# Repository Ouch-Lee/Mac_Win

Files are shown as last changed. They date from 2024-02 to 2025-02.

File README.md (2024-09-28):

# Mac_Win
This repository is used to share files between my mac and win

actually it has been the primary repository for surgical robot project

## TODO

一个完整的手术机器人系统的设计主要包括如下内容：

* 机器人机构研究
* 机器人控制研究
* 图像引导和路径规划研究
* 人机交互研究。研究操作者、机器人、患者之间的人机交互操作机制，改善人机工效。

目前机械结构大致已经搭建完毕，后续主线任务不应该在机械设计上，而是搭建整个手术机器人系统

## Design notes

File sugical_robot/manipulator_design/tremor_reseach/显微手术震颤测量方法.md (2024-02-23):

# 显微手术震颤测量方法

[链接](https://onlinelibrary.wiley.com/doi/abs/10.1002/rcs.1717)

## abstract

* 震颤是执行精细运动任务（如显微外科手术）的主要障碍。传统测量不涉及代表显微外科手术的任务，都是静态测量
* 文章主要内容还是设计了量化手术测量的装置
* 8-12Hz，医生没有普通人明显
* 吹牛逼

## introduction

这个部分更为详细的介绍了手术中的震颤，文章强调什么呢，以前的人测量震颤都是关注静止的（**这里引用了很多论文要不粗略看一下？**），但是实际手术更多需要运动，如何在运动中分析抖动？（**那如果让我来写论文，我应该关注哪个呢？还是两个都关注？**）

## method

这个部分和上一篇论文基本一样

重点是如何去分析获得的信号

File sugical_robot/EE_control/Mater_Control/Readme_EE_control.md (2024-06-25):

# Readme_EE_control

这部分代码用于主端下位机STM32的控制；代码主要的目标是读取电机状态，控制电机运动，使用DMA读取多个传感器的信息

控制逻辑如下：

预动作：先关闭后开启（**搞定**）

上电后电机回零到初始位置[a1, 0, 0, 0] （需要写位置控制代码）**已经实现了**

是否需要检查一下电机是否正常工作？

用手捏pincher两次，作为开始控制的信号；当检测到gripper端编码器两次大幅度运动时（写检测和判断代码）

先实现DMA，然后写一下这个判断逻辑

* 成功实现DMA功能，现在将其移至到整体代码中-成功整合，遇到报错link 找不到函数的问题，因为没有添加对应=》成功整合代码；
* 

开始工作，进入while循环 ；首先使用50Hz的频率采样读取电机角度，编码器角度

* 电机角度读取的原理是CAN的中断，向电机发送命令帧后会自动返回回复帧，并通过中断获取；所以重点是处理函数：在处理函数里面根据第一帧的数据进入不同函数处理：
  * 多圈角度：0x92
  * 单圈角度：0x94
  * 编码器一堆字节：0x90
  * 电机状态：0x9C
* 将读取的12个角度编码，通过CAN发送到从端单片机（这里写好了，但是需要整理）
  * 将8+4存在同一个数组中，并使用CAN_send_函数发送（已经写好了，测一下延迟）

## 电机控制

需要借助电机实现的功能如下：

```C
float theta_0[2] = {0.0, 0.0}; // 假设两个编码器的初始角度都为 0 度
float theta_1[2] = {45.0, 55.0}; // 假设两个编码器的目标角度分别为 45 度和 55 度

// 编码器状态枚举
typedef enum {
    AT_THETA_0,
    MOVING_TO_THETA_1,
    AT_THETA_1,
    RETURNING_TO_THETA_0
} EncoderState;

// 用于记录每个编码器达到theta_1的次数
int theta_1_reached_count[2] = {0, 0};

// 检测编码器是否到达目标角度，考虑误差范围
bool is_at_theta(float current, float target, float error_range) {
    return fabs(current - target) < error_range;
}

int main() {
    printf("Starting encoder movement detection.\n");

    // 初始化编码器状态
    EncoderState state[2] = {AT_THETA_0, AT_THETA_0};

    // 无限循环，直到两个编码器都达到theta_1两次
    while (true) {
        for (int encoder_id = 0; encoder_id < 2; encoder_id++) {
            float current_angle = read_encoder_angle(encoder_id);

            switch (state[encoder_id]) {
                case AT_THETA_0:
                    if (current_angle > theta_0[encoder_id] + (theta_1[encoder_id] - theta_0[encoder_id]) / 2) {
                        state[encoder_id] = MOVING_TO_THETA_1;
                    }
                    break;
                case MOVING_TO_THETA_1:
                    if (is_at_theta(current_angle, theta_1[encoder_id], 0.1)) { // 假设误差范围为0.1度
                        state[encoder_id] = AT_THETA_1;
                        theta_1_reached_count[encoder_id]++;
                    }
                    break;
                case AT_THETA_1:
                    if (current_angle < theta_1[encoder_id] - (theta_1[encoder_id] - theta_0[encoder_id]) / 2) {
                        state[encoder_id] = RETURNING_TO_THETA_0;
                    }
                    break;
                case RETURNING_TO_THETA_0:
                    if (is_at_theta(current_angle, theta_0[encoder_id], 0.1)) {
                        state[encoder_id] = AT_THETA_0;
                    }
                    break;
            }

            // 检查两个编码器是否都已达到theta_1两次
            if (theta_1_reached_count[0] >= 2 && theta_1_reached_count[1] >= 2) {
                printf("Both encoders reached theta_1 twice. Exiting loop.\n");
                return 0; // 正常退出程序
            }
        }
    }
}
```

```C
    // 电机数据解码
    if (rxbuf[0] == 0xA1) {
        int16_t tau = (int16_t)(rxbuf[2] | (rxbuf[3] << 8));
        int16_t speed = (int16_t)(rxbuf[4] | (rxbuf[5] << 8));
        uint16_t position = (uint16_t)(rxbuf[6] | (rxbuf[7] << 8));

        // 根据接收到的ID更新电机角度值
        if (id > DEVICE_STD_ID && id <= (DEVICE_STD_ID + 5)) {
            // 更新received_data数组中的角度值
						switch (id) {
								case 0x141: {
										received_data[id - DEVICE_STD_ID - 1] = (double)position / 65535.0 * 360.0 - 185;
										break;
								}
								case 0x142: {
										received_data[id - DEVICE_STD_ID - 1] = (double)position / 65535.0 * 360.0 - 322;
										break;
								}
								// 可以根据需要添加更多的case语句
								default:
										// 可以在这里处理未匹配到ID的情况
										break;
		}
            
        } else {
            printf("Received message with unexpected ID: 0x%03X\n", id);
        }
    } else {
        printf("Received message with wrong header byte: 0x%02X\n", rxbuf[0]);
    }
```

使用读取多圈角度的命令，出现bug：当角度为负数时不是负数而是

* 该问题已经得到解决，但是原理我并不懂（后面需要继续搞明白这一块

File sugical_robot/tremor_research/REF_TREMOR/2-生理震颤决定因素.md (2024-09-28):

# 生理震颤决定因素

## 摘要

目的:外围机械共振因素和中枢机制可能在生理性震颤(PT)的产生中发挥作用，这一点已经得到了很好的证实。此外，还假设受试者的年龄和性别等属性可能会影响PT。本研究旨在量化这些对PT的影响。**（主要是研究上述因素对生理震颤的影响）**

研究方法：对117名20至94岁的正常受试者进行生理手和手指震颤测量，使用加速度计和前臂弯曲肌和伸肌表面肌电图记录。在有体重和没有体重时测量手部震颤，在手臂伸出、前臂支撑和手支撑时记录手指震颤。测量每位受试者的手体积和握力。**（测量手部震颤的方法可以作为学习目标）**

结论：

增加惯性(平均5.2 Hz)可显著降低手部震颤频率(平均7.7 Hz)，且与手量呈负相关，而与握力无关。手指震颤显示，根据手臂的位置，最多3个和至少2个不同的频段(1±4,6±11和15±30 Hz)分别反映整个手臂，手和手指的共振频率。

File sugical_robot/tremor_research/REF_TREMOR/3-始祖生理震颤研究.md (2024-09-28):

# 始祖生理震颤研究

## 简介

简介主要引出论文话题——有人觉得生理震颤主要由脊髓决定，有人认为是大脑，但是频率确实是10Hz左右

研究方法：

* 使用加速度好于位置
* 介绍了很多当时技术局限性使用的方法，已经不具有实时性了

## 结论

正常成人生理性震颤的运动速率和记录部位与频率的关系

通过记录腕关节肌肉信号，得出振动频率的结论——7-12Hz

除了手部，身体其他位置也会存在振动

肢体放在偏下时的振动振幅大于被抬起来

手腕/肩膀添加负重时，抖动会发生改变

小孩也有抖动，这些抖动发生在腕部、肩膀、脚踝，膝盖（以前没人做过）

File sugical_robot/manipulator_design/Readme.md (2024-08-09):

## 论文说明

2-Technical review of the da Vinci surgical telemanipulator：达芬奇手术机器人专利

3-A novel pich grip design：设计了一种权衡手指捏握和手柄的grip

4-DaVinCi_patent：达芬奇手术机器人专利

5-hand_fitague_research：很早的一篇文章（1979），研究了手部在几种状态下肌肉震颤情况，量化的方式是通过记录什么肌电图

6- 一篇解剖学相关的文章，论述了手部的两种姿态

7- 一篇关于pincher grip的专利

8-一篇介绍仅紧凑master manipulator设计的论文

9-[哈工大一遍优化主端手术机器人的文章](https://ieeexplore.ieee.org/abstract/document/8848374)

10-[稍后再看](https://link.springer.com/article/10.1186/s12938-018-0601-6?fromPaywallRec=false)

11-[一篇把gripper讲明白了的IROS](https://ieeexplore.ieee.org/document/8202159)

12-[还有专门研究gripper的？](https://www.researchgate.net/publication/271547893_Effect_of_load_force_feedback_on_grip_force_control_during_teleoperation_A_preliminary_study)

13-[很捞但至少它是真的做gripper的](https://ieeexplore.ieee.org/abstract/document/7177760)

14-[一篇和我做的很像的all-joint-control的master device](https://link.springer.com/article/10.1007/s11548-016-1352-0)

15-[一种圆柱体gripper？](https://ieeexplore.ieee.org/abstract/document/7759149)

16-[4DOF抓手力反馈研究](https://ieeexplore.ieee.org/abstract/document/4145189)

17-[MIS抓手力反馈实现](https://ieeexplore.ieee.org/document/10058553)

18-[自己做一台达芬奇](https://ieeexplore.ieee.org/abstract/document/6907809)

19- [master_console_review.pdf](master_console_review.pdf) 

### combined-grip-handle grips design

这篇文章讨论了目前主流的两种grips——pinch类型（以达芬奇手术机器人为代表）和power类型（以sigma7）为代表分别存在优缺点，前者精度更高，但是使用时更加费力；后者则刚好相反，因此作者通过一些设计权衡两者之间的优缺点

首先提出了将pinch安装在handle上的概念，通过一个转动副和一个移动副连接（被动的没，相当于一个调节的作用），通过设计对照试验，验证了有这个自由度好一点

整篇论文大部分时间都在介绍实验以及实验结果，通过多组对照组，得出时间相关的结论

### Prehensile Movement of HUman hand

该文研究了人类手部的可动性能力，包括不同类型的握持方式和手腕的运动。该文的主要结论是，手部的握持方式和手腕的运动是根据任务目标来选择的，任务的要求可以分为力量和精度两个方面，而手部的可动性能力可以满足这些任务的要求。此外，该文还指出，人类手部的简单和通用性质是其进化的结果，而过度专门化会限制手部的其他可能用途。

## Hamlyn CRM: a compact master manipulator for surgical robot remote control

introduce：该部分先介绍了主流手术机器人主要由三部分组成：a master control console with interactive manipulators, a slave surgical robot with articulated instruments and a feedback system with vision and other sensing modalities.；之后介绍了主从结构的特点，但是不够紧凑，所以这篇文章用了传感器融合技术；同时重点介绍了他们手术机器人模型的映射策略

* 机械结构

  通过matlab的运动简图可以看出大致原理，三个正交轴实现手朝向的变化，一个线性轴+万向节实现空间位置改变

* 运动学

  运动学较为简单

* 传感器融合

  * 两个imu+两个霍尔传感器
  * 如何进行处理传感器数据

* 末端添加光标，结合NDI光学跟踪系统验证末端精度

* 主从映射策略

  * 主从系统那个图做的很好，很具有借鉴价值
  * 所有传感器信息使用到了ROS发布
  * 介绍了 主-视觉坐标系-从坐标系之间的变化（由于还没有研究视觉坐标系，这里先跳过）
  * 映射模式：位置模式采用P模式，姿态采用绝对（直觉映射）和增量控制两种模式，两者各有优势
  * 

## 11-Master manipulator designed for highly articulated robotic instruments in single access surgery

**introduce**：因为主从机器人的性能很大程度取决于master device 的性能，这个设计是为了解决工作空间不匹配，以及缺乏重要关节被限制的信息（可能他就是想说明同构关节的好处，能够让操纵者知道哪个关节受到了限制）；关节处设计一个力传感器主意挺不错，可以通过力的方向判断运动方向，结合电机辅助操纵者运动

introduce: 先介绍了手术机器人主从系统的被广泛应用的原因；后面介绍为什么要注重主端的设计：

An advanced slave system composed of highly dexterous instruments will ultimately not perform to its full potential if paired with an inadequate master system.

然后提出目前主流的手术机器人都是基于task space去设计，这样的缺点是 mismatch ，以及一些缺点

所以,the use of a dvice-specific master manipulator commanding the slave robot is **joint space** can be an attactive alternative。

后面介绍了几种joint-control的主端设备，但是缺点竟然是关节都是被动的？

**manipulator design:**

具体介绍了机械结构

**Workspace Analysis：**

绘制了主从工作空间的灵活程度（我是不是应该也分析一下？

Control system：

* 为了提示操纵者每个关节快到边界了，添加一些阻力
* 自身重力补偿
* 摩擦力补偿，这个等到自己要做的时候再仔细的看

## 12-研究gripper握力的文章

这篇会议论文刚好就是我现在在做的东西，可以带着critical thinking的眼观来审视这篇论文

文章主要想解决的问题是目前手术机器人的抓取严重依赖视觉反馈，力太大夹伤了，力太小又容易脱落。所以这篇文章就是研究如何控制握力

之前的工作是证明人手在抓取时手指的窝里和手上的载荷相关；视觉仅能进行预估，不如触觉准确；还有一些别人做的实验，说明平移的反馈了不如抓取的反馈力，这不是废话吗

## 16

1. **研究目的**：文章旨在确定在执行远程操作任务时，握力反馈与笛卡尔（平移）力反馈对操作者的影响。
2. **系统开发**：研究者开发了一个系统，为3自由度（DOF）的Phantom触觉设备主机增加了额外的握力反馈DOF，并且在Phantom触觉设备从机的每个“手指”上增加了6-DOF力/扭矩传感。
3. **实验设计**：用户在执行一个软性插孔任务时，会接触到不同的力反馈条件：(1) 全力反馈，(2) 仅平移力反馈，(3) 仅握力反馈，以及 (4) 无力反馈。实验结果显示，在增加握力反馈的3-DOF远程操作器中，平移和握力的施加水平是解耦的，这可能是由于内部和外部手部力的动力学是解耦的。
4. **远程操作器的挑战**：当前的远程操作器，包括手术远程操作器，并不向用户提供完整的力反馈。力传感器的尺寸、消毒和生物相容性限制了在手术环境中使用从机器上完整的力感应的可行性。
5. **实验方法**：五名右手受试者使用4-DOF远程操作器执行简单的操作任务，即抓取一个矩形泡沫“插孔”并将其插入泡沫块中的矩形孔中。实验中提供了四种不同的力反馈条件，每种条件都由受试者随机顺序重复五次。
6. **实验结果**：方差分析（ANOVA）表明，力反馈显著影响平均施加的平移力和平均施加的握力（p < 0.0001），但对完成任务的时间没有显著影响（p = 0.144）。实验不支持假设1和假设2，即平移力反馈不会显著影响施加的握力，反之亦然。
7. **结论**：文章提出了一个使用两个Phantom触觉设备的4-DOF远程操作器，该设备具有可附加的夹持机构，能够提供4个DOF的力反馈。研究表明，在没有提供力反馈的DOFs中，平移力反馈和握力反馈在调节力的能力上是解耦的。在需要最小化Cartesian力反馈和握力反馈的情况下，显然需要全反馈。
8. **未来工作**：未来的研究将包括对能量观测器和环境建模的研究，以减少部分力反馈对用户的负面影响，并确保具有传感器/执行器不对称性的远程操作器的稳定性。

文章的研究对于理解和改进远程操作器，特别是在手术远程操作领域的力反馈设计具有重要意义。

### 商用手术机器人

根据搜索结果，以下是一些国外与达芬奇手术机器人类似的腹腔镜手术机器人：

1. **图迈®腔镜手术机器人系统**：由上海微创医疗机器人（集团）股份有限公司研发，已获得欧盟CE认证，可用于泌尿外科、普通外科、胸外科、妇科内窥镜手术。该机器人具备力觉感知呈现组件、多层安全防护架构和先进的成像系统，提供10倍光学放大的高清视野，实现裸眼3D成像 1。
2. **MIRA 微型手术机器人**：由Virtual Incision Corporation推出，是首个用于腹腔镜手术的微型机器人，重量仅有900克，通过肚脐内的单个切口完成手术。MIRA平台专注于微创结直肠和下消化道手术，具有一次性末端执行器仪器、双极抓手和单极剪刀，以及柔性尖端机器人相机 2。
3. **美敦力的Hugo**：美敦力公司推出的Hugo手术机器人，获得CE批准上市，专为泌尿科和妇科手术设计。Hugo是一个模块化的多象限手术平台，结合了腕式器械、3D可视化和Touch Surgery Enterprise，旨在降低成本和使用障碍，提高外科手术机器人的普及率 9。
4. **Medrobotics公司的Flex Robotic System**：该系统可以导航接近180度的路径到达具有挑战性的手术目标，外科医生可以从稳定的手术平台部署3毫米铰接器械，扩大执行手术范围。该系统已于2014年获得欧洲CE标识，2015年获得FDA批准 2。
5. **TransEnterix公司的Senhance数字腹腔镜手术系统**：具有压力感知和触觉反馈系统，通过压力警报增强医生的感知。该系统在欧洲和日本获批上市，并已提交FDA审查 2。

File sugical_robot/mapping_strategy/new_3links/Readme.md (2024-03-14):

# Readme

* get_continuum_T: 求单个连续体末端相对于base的其次变换矩阵
* extended_two_links: 用于求解添加extended坐标系后二连杆的T（好像）
* check_two_orien: 看起来像在验证没有添加delta_x 前的映射
* check_paper_DH: 似乎添加delta_x后的映射，运行前需要先运行extended_two_links
* my_DH_matrix ： 用于求解主端运动学的其次变换矩阵

最终结果在 "Show rotation.m" 文件中展示

在运行该文件前，需要先运行“extended_two_links”+“check_paper_DH”

### STM32串口数据处理

* 传输的数据太多了，所以先进行了简单的采样处理 sampling_array 函数
* get_end_position 传入采样后的数据
  * 需要处理一下角度
  * get_one_P中计算全是整数的问题，将sym计算得到的数换到另外一个T_matix里面就行
  *

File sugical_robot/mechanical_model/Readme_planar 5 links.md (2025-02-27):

# Readme_planar 5 links 

提出第二代base结构，使用平面五连杆机构

## 平面五连杆结构的优势

## 运动学模型

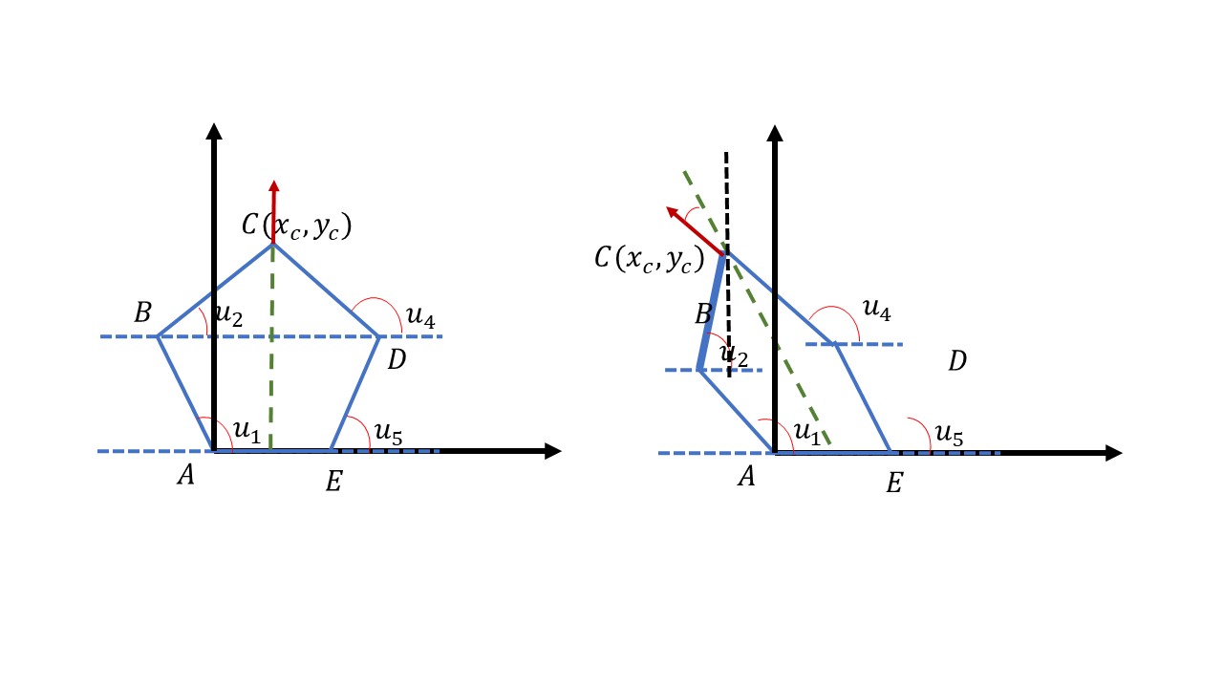
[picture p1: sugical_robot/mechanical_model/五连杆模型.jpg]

$$
x_b = l_1 * cos(\lambda_1),
    y_b = l_1 * sin(\lambda_1); \\
    x_d = l_5 + l4 * cos(\lambda_4),
    y_d = l_4 * sin(\lambda_4); \\
    BD = \sqrt((xd - xb)^2 + (yd - yb)^2) \\
$$

$$
\phi_1 = cos^{-1}(\frac{l_2^2 + BD^2 - l_3^2}{2*l_2*BD}); \\
\phi_2 =  tan^{-1}(\frac{yd - yb}{xd - xb});  \\
\alpha_2 = \phi_1 + \phi_2
$$

具体的实现可以参照[代码](E:\GitHub\Mac_win\Mac_Win\sugical_robot\mechanical_model\plannar_5_links\planar_5_bar_foward_my.m)

为了满足规范的角度规定（如下图），得到新的公式结果：
$$
\alpha_2 =( \phi_1 + \phi_2 ) - \alpha_1  \\
\alpha_3 = \pi - ( \phi_3 - \phi_2) - \alpha_4
$$



根据论文里面的公式，可以求解末端端点，但是

https://journals.sagepub.com/doi/full/10.5772/45683

[目前发现最早动力学推导论文](https://www.sciencedirect.com/science/article/pii/S0957415804000625)：现在没心情看

[用在打印机上的平面五连杆](https://www.sciencedirect.com/science/article/pii/S0736584512001214)：机械结构设计可以参考

## matlab实践

https://ww2.mathworks.cn/help/sm/ug/five-bar-robot.html

https://blog.csdn.net/qq_36014310/article/details/76924980

## 工作空间分析

得到五连杆的正向运动学模型后，通过循环的方法似乎可以得到原始的工作空间

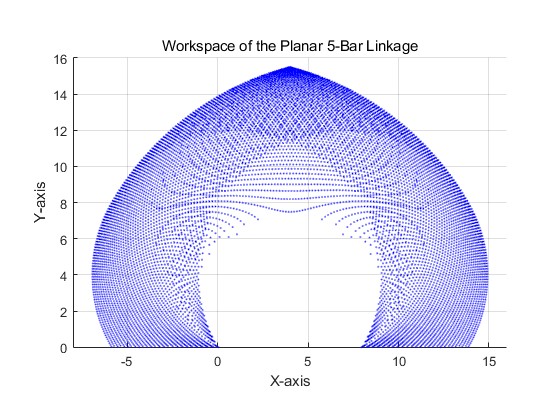
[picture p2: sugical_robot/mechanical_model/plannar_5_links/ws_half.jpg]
ws_half


上面是不考虑对称位型的工作空间，下面红色是添加对称位型后的工作空间；其实也就多了中间一小部分，因此为了简化问题，这一部分确实可以舍弃，因此【需要考虑一些机械限位】

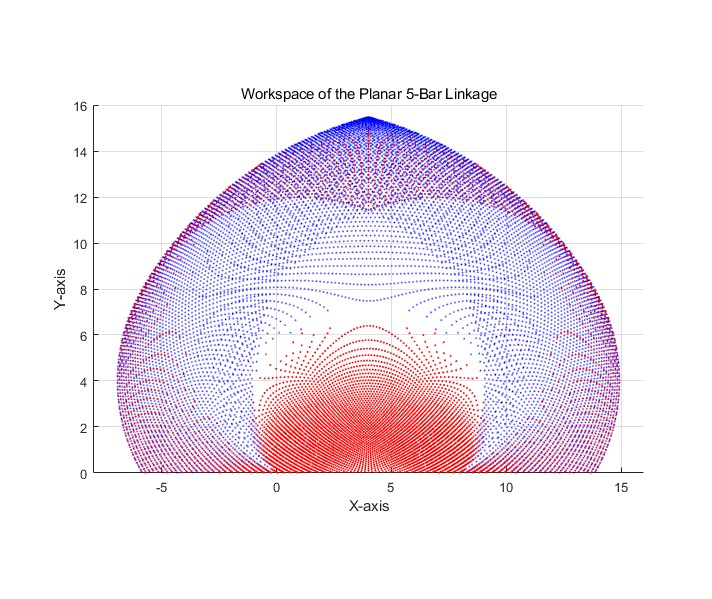
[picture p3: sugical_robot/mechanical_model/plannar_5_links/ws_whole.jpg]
ws_whole


相比之下，通过缩短两个关节之间的距离，可以明显增大工作空间

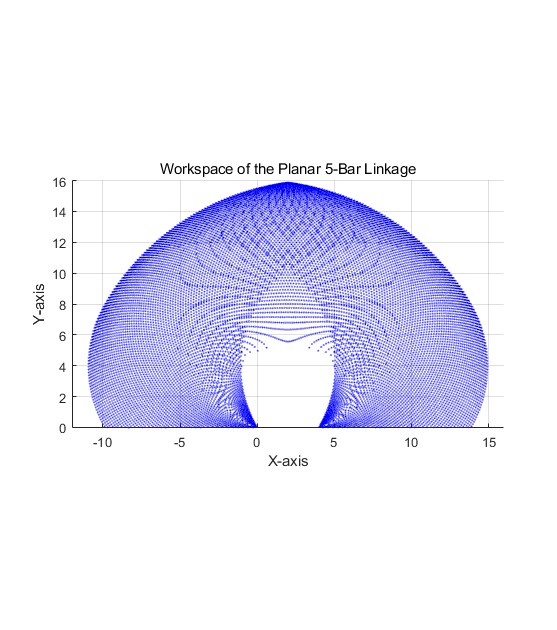
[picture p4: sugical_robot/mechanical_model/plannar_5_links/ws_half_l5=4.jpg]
ws_half_l5=4


## 结构设计

[日本轴承](https://detail.tmall.com/item.htm?spm=a21n57.1.item.2.5ae5523ccEkvGh&priceTId=215041aa17187626641891929e1a65&utparam=%7B%22aplus_abtest%22:%22dd09899006de88438ba666a726a98146%22%7D&id=668412789062&ns=1&abbucket=8&skuId=4809943724973)

[便宜一点的](https://detail.tmall.com/item.htm?spm=a21n57.1.item.48.5ae5523ccEkvGh&priceTId=2147bf3617187636843351715e1a6c&utparam=%7B%22aplus_abtest%22:%22d2c9aabf4e6b96251b2b7bc117ae65de%22%7D&id=611796709407&ns=1&abbucket=8&skuId=4777422306655)

目前计划选择  I5o14h5的 => 改为 I5O16H5，根部使用标准轴承 7000AC: 10 26 8

深沟轴承换为角接触轴承 需要 10 -15 个

轴承：

* [x] 推力轴承i6o19 x 6
* [ ] 

需要的螺栓：

* [x] M6 x 18 / 20 + 30
* [x] M4 x 26 + 20
* [x] m3 x 5
* [x] m2.5 x 10 \12
* [x] m2 x 20 + 8
* [x] m2 沉头 x 5
* [x] M6螺母
* [x] M4 螺母
* [x] phi6塞打螺栓x20
* [x] phi6塞打螺栓x25
* [x] phi6塞打螺栓x40
* [ ]

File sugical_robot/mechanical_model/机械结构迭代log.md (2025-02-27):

# 机械结构迭代log

5-26号装完第一版以后存在如下问题

* 配重不准（）

* [x] 替代电机的部分连接不稳：没有2.5螺母，轴承过盈效果不佳，最重要pitch连杆固定不住

  添加了2.5螺母，pitch连杆添加螺母固定，增强轴承过盈效果

* [x] 编码器孔是4

* 电机安装座通通错位了

* [x] 横向电机螺栓未考虑 用16的

* [x] 纵向齿条加固件干涉

* [x] 横向电机没有螺母

* 切割板没有电机安装孔，导轨安装孔为M3

* [x] 手柄main部分和齿轮干涉

修改

* 首要需要解决的是main部分需要：

  * [x] 编码器固定孔
  * [x] 上下螺母槽
  * [x] 齿轮卡住的问题
* 2.5螺母
  * [x] 购买
* 齿条

## 8-11完成初步结构后完善

### 悬臂梁配重

经过大致计算，关于转轴的力矩为 8360 g*cm，整体重量为750g，等效质心距离为11.15cm， 平均到两个杆

经过力学分析：
$$
F_N - F_p = F\\
F_N * l_2 + F_p * l_1 = F*L \\
F_N * (l_1 + l_2) = F*(L + l_1) \\
F_p * (l_1 + l_2) = F*(L-l_2) 
$$

通过有限元分析，使用铝合金 7075 足以满足要求，不会产生明显偏转

除此之外，添加一定重量的配重，目前的想法是每边添加一个500g的配重

之前只考虑倾覆力矩其实还有很明显的压力，所以需要添加一个推力轴承，这样也不会出现明显下倾的趋势了

* 电机与转轴适配性的问题：

目前的电机不一定能满足控制要求，但是理论上只要控的好，可以收敛不抖动；为了考虑性能，还是需要做到转轴适配不同电机？

感觉成本也不是很高，一体化可以避免配合间隙，尽量一体化

* 左右需要错开
* 旋转不能碰到base，但是杆长又不能延长了，所以得有一个偏置

## 整体机加工

之前三连杆部分采用的树脂3D打印，时间长了褪色，而且存在虚位较大的问题；

因此在重新设计了符合机加工的零件后，绘制了对应的[加工图纸](E:\master_console_ver3\图纸\2025-1加工)

第二批机加工需要准备零件：

| 零件          | 数目          |      |
| ------------- | ------------- | ---- |
| 杯头M3 x 10   | （12+8+8）x 2 |      |
| M3x6x0.8 垫片 |               |      |
| 平头M2.5 x 8  | 5x4 x 2       |      |
| M3手拧螺丝    | 4             |      |
| 平头M3 x 6    | 8 x 2         |      |
| 平M2X6        | 8x3           |      |
|               |               |      |

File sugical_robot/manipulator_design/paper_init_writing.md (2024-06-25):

# 论文撰写—一种应用于NOTES手术机器人的外骨骼式主操作台设计

## 摘要

这篇文章主要介绍一种应用于自然孔腔手术(NOTES)手术机器人的外骨骼式操纵台的设计。手术机器人系统整体采用主从式驱动映射策略，设计该结构的目的，力求保证手术医生手臂舒适、不影响手术医生手部自由运动的情况下，将手术医生手臂与手动作以直觉的方式映射到从端手术机器人。文章主要介绍该装置在结构上的创新性，舒适性，及其可行性。并从软件和硬件两个方面介绍了该装置在消除手术过程中手部颤抖的贡献；根据预期的直觉映射策略，推导主端驱动空间到从端构型空间的映射关系，并在仿真中验证了映射的可行性。

**3-8：结建立的动力学模型 of master console，我们使用我们的设备对手部生理震颤提出了评估，and address the hand tremor from both software and hardware perspectives** 

通过分析主从端的运动学模型，我们建立了合适的mapping strategy, which showcases the system's intuitive operation.

## Introduce

_____

		自然孔腔内窥镜手术是一种借由内窥镜通过人体的自然孔腔到达病灶位置的外科手术，自1957年第一台光纤内窥镜成功完成诊断手术以来[1]，内窥镜技术得到广泛关注和发展，19世纪70年代人们开始设想借助内窥镜完成一些简易手术，1980年  Michael W.L. 首次对12名儿童和19名成人描述了“无需剖腹手术的胃造口术”(**这里改成英文**)[2]，验证了内窥镜手术的可行性，由此学者开始尝试使用内窥镜完成更复杂的手术，并于2005年被正式提出NOTES的概念[3]。相较于开放的剖腹手术，NOTES存在诸多优点，可以避免开放手术带来的伤口感染和切口疝的问题[4]，因此可以实现更快的术后恢复，减轻患者术后疼痛等问题。

		早期的NOTES通过内窥镜及其配备的简易活检设备实现，只能进行简单活检和组织切除手术，为了完成更为复杂的手术，学者们设计了多种用于NOTES的手术机器人，它们通常具有相同的配置，集成摄像头的内窥镜主轴和从远端分支的两个手术臂 ，如  EndoSAMURAI[5]，Cobra[6], K-flex[7]。操作三角测量在柔性内窥镜手术中的灵巧检查和操作中起着至关重要的作用，该角度可以定义为两个仪器之间的远端姿势向量[8]，受限于结构，上述手术臂为单段连续体通常不具有良好的三角测量性，ANUBIScope[9], A flexible endoscopic surgical system[10] 将出口展开提供被动的三角测量性。

		尽管NOTES手术机器人已经成了医疗设备领域的热门研究对象，但现有关于其操纵台介绍的文章较少。目前商业主流的操纵台，如达芬奇手术机器人[11]和Hugo[12]，其操作台均为6自由度，而大多NOTES手术机器人有4自由度，两者存在不兼容的情况。为了避免自由度冗余，早期类似于EndoSAMURAI和Cobra的手术机器人采用纯机械式的摇杆（[下图](https://link.springer.com/article/10.1007/s00464-012-2173-z/figures/1)），在实际手术中需要多个人配合操纵，过于简单的操纵台使得医生使用体验不佳，这样导致手术效率低，安全得不到保障。设计不良的界面会降低外科医生的人体工程学效果，并会阻碍机器人的接受度[13]，这一点在微创手术机器人设计中已经验证。   [KFLEX](https://onlinelibrary.wiley.com/doi/abs/10.1002/rcs.2078) 设计了一种简易的三联杆结构用于柔性臂的控制，可以实现更易让操纵者接收的“直觉控制”，但是结构设计过于简单，没有考虑人体工程学的问题，且没有考虑操作三角性的问题。

	受前人工作的启发，我们提出了一种可以控制三角测量性的内窥镜双通道手术机器人模型，它由远近两段连续体组成，近端的偏转提供主动的三角测量性，同时可以增加手术时的灵活性，近端和远端协作完成手术动作；并根据该模型自由度设计了一种外骨骼式的手术机器人操纵台，可以利用人体手臂的其中5个自由度一对一控制手术机器人的关节，实现高效的直觉控制。在进行第一版样机测试时发现操纵者手部存在明显的生理抖动，为了改善抖动引起的末端震颤，我们在硬件和软件层面提出了改善方法；通过建立主端两端运动学模型，我们推导了从操纵台的驱动空间到末端执行器构型空间之间的映射关系，并在matlab中验证了映射关系的正确性。

	本文的结构如下：在第二节阐述了主从两端自由度分布，以及对操作台的机械结构设计进行介绍；第三节主要关注在NOTES手术机器人在主端震颤过滤的东线；第四节推导了操纵台到柔性手术臂之间的运动学映射；第五节对全文进行了总结。

Flexible instruments with steerable heads and multi-instrument flexible devices are difficult to control manually using a single operator.[13](https://ieeexplore.ieee.org/abstract/document/9779312)

##  MECHANICAL DESIGN

### 主从端自由度配置

设想的从端手术机器人配置如下（Fig2(a)）：柔性机械臂搭载在双通道的内窥镜上，其近端连续体由同向的单元连接而成，在一对cable的驱动下可以朝两侧弯曲，以增大远端连续体之间的间距，提供较好的三角测量性；远端连续体相邻的单元正交排布，由两对cable驱动，具有两个方向偏转自由度，末端器械通过微型轴承连接在远端连续体上，具有绕轴旋转和开合的自由度。

主端操纵台的功能是精准捕捉并映射操纵者控制指令，力求满足人体工程学设计，避免影响手术医生上肢自由运动。合理的自由度布局能避免复杂的映射策略，使得外科医生直观的进行操作，以减少学习曲线并提高手术的安全可靠性[]，因此master console，末端执行器与人体手臂三者之间自由度分布与极为类似, 如fig2所示。这种布局使得surgeon和master console之间有较好的适配性的同时，又让surgeon能舒适的控制surgical arm。

三者之间自由度的联系如下：操纵者将手肘“固定”在“搭载台”上以后，利用肩关节和手肘关节配合实现前后和内外翻转运动，并驱动操纵台“搭载台”下的两个正交的平动关节，对应手术机器人末端的前后伸缩，以及负责调控三角测量性近端连续体的偏转；手指握在pincher formation处，配合手腕的关节实现yaw,pitch, rolling 三个方向的运动，驱动操纵台前端三轴交于一点的“三连杆”对应的旋转关节，实现执行端前端连续体的两个方向偏转及其末端手术器械的绕轴旋转。

备注：

2-26：自己修改了一遍，没有经过gpt润色

### 设备实现

___

操纵台两个正交方向的平动均由两根平行的**导轨滑块**（MGW9，中国江苏）实现，相对于K-FLEX中单个导轨的设计，间隔一定距离的平行导轨可以避免手臂搭载时压力产生的倾覆力矩，每对导轨上的板子多采用铝合金材料，通过验证可以满足强度校验；导轨带来顺滑移动的同时，也带来了系统不稳定的问题，轻微的扰动即可导致末端出现预期以外的运动，因此在上述结构基础上，每个方向的平动都使用连接了**无刷电机**（KMTECH，中国上海），并使用齿条齿轮机构作为传动机构。相对于编码器，在每个关节处配置无刷电机的好处是，关节抗外界干扰能力更强，同时电机能够实现更为复杂的控制，使得操纵台不仅是一个运动采集机构，同时也能实现一些交互控制，例如较为成熟的变阻抗控制，使得平动的关节的可以灵活的改变。

与hand交互的三连杆，在原理上它与K-FLEX一样，但在此基础上我们做出了许多修改：首先我们额外增加了两条镜像连杆以及一些**“配重砝码**”，这样使得外部更美观，更重要的是增加结构的平衡性和稳定性，除此之外，更好的力量传递和控制是双边结构相对于单边结构的一个重要优势，双边结构可以实现分布式力量传递，即将力量从两侧均匀传递到目标区域，是可以让操纵者的操纵更加顺滑。

前人设计的“finger gripper”结构通常是搭载在rolling连杆上的一个钳子形状的gripper，一般操纵者使用大拇指和食指握住以控制末端器械如镊子的开合，这使得其他手指则处于蜷缩的空闲状态没有被利用，我们提出了一种创新的【pincher formation】结构(Fig3(b))，给剩余三个手指提供抓握的同时，将它们利用起来完成其它的任务。这是一个类似于手枪把手的结构，操纵者可以使用中指扣住【扳机】，控制一些功能的开关，如手术时所必须的冲洗，吸收积液，充气等操作，为了灵活切换上述功能，在把手下端设置了一个【轮盘】来切换上述功能。上述零件受力较小，因此我们使用光造型树脂作为材料并以3D打印的方式制作，这种材料具有高精度、表面光滑、细节丰富、打印速度快以及可用于复杂结构的优点。

上述整个结构可以简化为串联的五连杆，Serial kinematic configurations的优点包括：机械结构更简单，有利于制造并减少潜在故障点，从而减少所需的维护量[ ]，同时运动学模型和动力学模型较为简单，为后续人机交互控制降低难度。

无刷电机的内部集成了驱动板，使得整体结构更为紧凑，且驱动板内部集成FOC算法，仅需向其发送指令即可实现多种模式的控制，包括增量位置控制，绝对位置控制，速度控制和力矩控制；同时电机还集成了精度为18bit的绝对值磁编码器；我们使用STM32嵌入式单片机作为控制板，通过CAN通信协议控制和读取电机的状态。

Here are the translations for the phrases you provided, suitable for use in a table and aiming for a natural and concise English expression:

yaw link rotation

- 肘部前后运动: Elbow Flexion/Extension
- 肘部左右摆动: Elbow Abduction/Adduction
- 手腕左右偏转: Wrist Ulnar/Radial Deviation
- 手腕上下偏转: Wrist Flexion/Extension
- 手腕绕轴转动: Wrist Pronation/Supination
- 底座前后平移: Base Anteroposterior Translation
- 底座左右平移: Base Lateral Translation
- 手术臂伸缩: Surgical Arm Extension/Retraction
- 近端展开: **Proximal Unfolding**  双臂展开怀抱和对应的反义词用英语怎么说
- 远端左右偏转: Distal Lateral Deviation
- 远端上下偏转: Distal Vertical Deviation
- 手术器械绕轴转动: Instrument Rotation
- 手术器械开合: Instrument Articulation/Open-Close

These terms are succinct and are commonly used in descriptions of mechanical movements, particularly in the context of robotics and biomechanics.

## 手部震颤抑制

震颤过滤是所有遥操纵的手术机器人需要共同面对的问题，在设备性能优良的情况下，操纵者手部的震颤成为了震颤的主要来源。这种震颤被称为生理性震颤（Physiologic Tremor），一种生理性现象，正常情况下每个人都会经历的微弱的震颤或颤动。这种震颤的频率在8-12Hz之间，通常肉眼通常无法感知，但在手术的条件下，生理性震颤是不可忽视的不利因素，The trend towards the use of ‘minimally invasive surgery’ also tends to amplify tremor effects, due to the longer lever-arm action of typical laparoscopic instruments[3-1].

Tremor mitigation is a critical challenge in teleoperated surgical robotics. When the equipment performance is excellent, the tremor of the operator's hand becomes the main source of tremor. This tremor, known as Physiologic Tremor, is a physiological phenomenon that everyone normally experiences as a weak tremor or flutter. The frequency of this tremor is between 8-12Hz and is usually invisible to the naked eye. However, under surgical conditions, physiological tremor is a disadvantage that cannot be ignored. The tremor effects are amplified, due to the longer lever-arm action of typical laparoscopic instruments.

为了对surgeon的手部Physiologic Tremor进行evaluation，首先需要记录震颤活动，通常 accelerometry, electromyography (EMG), and other signals (such as force or gyroscopic measurements) are acquired, digitized through an analog-to-digital board and analyzed. 这种方法的问题是设备测量精度不够高，不能直接反应手部震颤的效果。在这里我们让surgeon手握"finger gripper"，通过记录各个关节的位置信息，结合master console的正向运动学，计算末端在空间中位置的变化，从而记录手部的震颤。

【图片1：初步震颤】【图片2：悬空15min后震颤结果】

为了减弱指端生理震颤为手术带来的的影响，首先我们引入了卡尔曼滤波算法，在软件层面上削弱震颤信号的波形

### 自适应卡尔曼滤波

单个电机的角度信号可以看作一阶系统，建立其状态方程及其对应的参数如下：
$$
\begin{cases}
x_k = x_{k-1} \\
        y_k = x_k
\end{cases}
$$

$$
F_k = 1; \quad H_k = 1; \quad G_k = 0; \quad u_k = 0;
$$

$$
公式1；
$$
借助卡尔曼滤波算法进行迭代，可以较为明显的平滑由于生理震颤产生的抖动信号；
$$
公式2
$$
卡尔曼滤波作为最为人知的滤波算法具有适应性强、有效地处理噪声和不确定性、计算效率高的优点[ ]。但是该算法存在两个最缺点，首先它像PID控制一样，需要对公式2中的参数Q与R进行手动调试；其次该算法无法兼顾精度和滤波效果，Q与R的比值会影响滤波结果，比值越小表示预测值的权重越大，最终结果抗干扰越强，但是会丢失一定精度；反之，比值越大越靠近标准值，滤波的效果越不明显。对前一个问题，前人已经提出了许多改进的自适应卡尔曼滤波算法，对于后一个问题，我们在这里提供了一种简单的模型，通过记录前后两次采样角度差值的方法，简易的区分操纵波形和噪声，并根据差值实时修改Q与R：

**简化后：**

卡尔曼滤波可以有效的处理噪声，并具有计算高效的优点[ ]，但是该算法也存在两个问题，一方面公式2中的参数Q和R需要通过经验调试，另一方面滤波在平滑噪声的抖动时也会使得正常的操纵动作失真，（Fig_）；我们提出了一种自适应的改进KF算法模型，可以有效的避免上述情况；
$$
公式3
$$
其中avg为经验值，通过记录多次噪声取平均值而得，因此diff 与avg的比值表示信号振幅的大小，较大时表示操纵波形，较小时为噪声。图---对比了传统卡尔曼滤波与改良后自适应卡尔曼滤波的效果，图中可以明显看到改良后滤波算法即避免了传统滤波算法引起的失真，又达到了消除抖动信号目的：由于操纵指令和震颤的幅度相差很大，印使用$\alpha$ 记录前后两次位置的差值，差值小表示抖动，通过减小Q和增大R增强滤波效果，反之差值大时避免滤波影响输入指令，对应模型的结果展示在图_ 中。

图

The angular signal from an individual motor is modeled as a first-order system, with its state equation and related parameters detailed subsequently.

Employing the Kalman filter algorithm iteratively allows for the noticeable smoothing of jitter signals induced by physiological tremors. Renowned for its adaptability, effective handling of noise and uncertainties, and computational efficiency, the Kalman filter, however, faces two significant limitations. Firstly, akin to PID control, it necessitates manual adjustment of parameters Q and R, as delineated in equation 2. Secondly, achieving a balance between precision and filtering efficacy proves challenging. The filtering outcome is influenced by the Q-to-R ratio, where a lower ratio signifies a greater emphasis on the forecast value, enhancing interference resistance but sacrificing accuracy. In contrast, a higher ratio approximates the standard value more closely but diminishes the filter's effectiveness. While numerous adaptive Kalman filter enhancements have been proposed to overcome the first limitation, we address the second by introducing a straightforward model. This model easily differentiates between control waveforms and noise by recording the angular difference between two successive samples, thereby allowing for the real-time adjustment of Q and R based on this discrepancy.

### 搭载式

生理抖动产生的一个原因是手部悬空[ref]。通过观察可以发现，相较于手臂悬空状态，手臂被托举时操纵者手指末端的抖动幅度和频率更小，因此商业微创手术机器人的操纵台大多都设计了小臂托衬结构，该设计的另外一个优点是缓解手术时手臂维持长时间悬臂的疲劳。我们通过采集两种状态下电机的角度信息，计算出操纵台末端位置信息，并将其可视化在图中。

【这里需要实物，实验和分析】

手臂长时间滞空导致的肌肉疲劳会加剧生理抖动，这也是为什么大多商业的微创手术机器人的操纵台配备了小臂托衬结构，这里我们设计了一个肘部托举结构，其作用除了托举操纵者手部，同时也作为一个“操纵杆”用于控制操纵器在正交导轨上的位置。为了防止操纵者在移动手肘的过程中不产生相对滑动导致脱落，这里设计了一个“紧固”结构，其工作原理如下：在操纵者将手肘搭载在“carrying disc”上后，在重力的压迫下，“carrying disc”随直线轴承向下运动，该运动由连杆传递到sliders，并通过连杆使一端固定的“four link”产生变形，该变形的最终结果是“elbow protector”向内收缩，从而加紧操纵者的肘部，当操纵者想脱离该结构时，将肘部竖直向上抽离即可。这样就做到了肘部在“穿戴”与“抽离”之间的自由切换。

有一个致命的问题是，目前第二代的样机仍在搭建中，虽然能通过肉眼很直观的察觉到托举结构对手部震颤的改善，但缺少严谨的实验和实验结果来论证该结论，但这个空缺会在短期内完善。

Muscle fatigue caused by the arm being suspended in the air for a long time will aggravate physiological jitter. This is why most commercial minimally invasive surgical robot consoles are equipped with a forearm support structure. Here we have designed an elbow support structure, whose function is in addition to lifting. The operator's hand also serves as a "joystick" to control the position of the manipulator on the orthogonal guide rail. In order to prevent the operator from relative sliding and falling off when moving the elbow, a "fastening" structure is designed here. Its working principle is as follows: after the operator places the elbow on the "carrying disc",  under the pressure from the gravity of arm, the "carrying disc" moves downward with the linear bearing. This movement is transmitted to the sliders by the connecting rod, and deforms the "four link" fixed at one end through the connecting rod. The final result of this deformation is that the "elbow protector" moves toward Contraction inward to tighten the operator's elbow. When the operator wants to escape from the structure, he can pull the elbow straight up and away. In this way, the elbow can be freely switched between "wearing" and "taking off".

A fatal problem is that the second-generation prototype is still under construction. Although the improvement of hand tremor by the lifting structure can be intuitively detected with the naked eye, there is a lack of rigorous experiments and experimental results to prove this conclusion. This vacancy will be completed shortly.

## mapping strategy

这一部分主要介绍从主端操纵台的驱动空间[theta 1 ... theta 5] 到从端构型空间的映射策略，也即在检测到操纵者输入的控制指令后，从端柔性臂应该调整到什么位型。在手术机器人领域，目前主流的主从映射策略是保持主从两端姿态和位置相同：通过主端正运动学计算目标位姿，再使用从端逆运动学求解从端驱动空间。但是由于目前结构为5自由度，**为欠驱动状态（**Underactuated），因此主流方法不适用。我们采取的映射策略是保证主从两端的姿态保持一致同时伸缩按比例缩放，实现较好的“直觉操纵”。为了简化映射的复杂度，我们采用解耦的方法，将整体映射策略分远近两段的子映射，这个方法是可行的，在保证每个子映射策略符合“直觉操纵”的情况下，整体依然符合“直觉操纵”。

Fig.3 显示了主从系统的integrated kinematic drawing。对于主端刚性连杆结构，我们沿用DH标准为每个关节配置了坐标系，并构建了对应的DH table；

对于从端柔性连续体，使用常规的DH会带来巨大的计算复杂度，这里我们采用更适用于连续体建模的常曲率模型[ ]。在常曲率模型中，使用ks描述连续体偏离轴心的偏转角度，使用phi描述因为两个正交偏转叠加后产生的绕轴转动角度。对于如近端单自由度的连续体，phi可以是视作0不变。

前面两个自由度的运动较为简单，且两个映射完全解耦，因此分别进行简单的线性映射即可：

主端console纵向平动与从端柔性臂的“伸缩“，以及主端横向的平动与柔性臂”近端偏转“的映射可以完全解耦，分别进行简单的线性映射即可：
$$
公式
$$
其中theta_max为近端连续体偏转的量程，dmax为导轨移动量程；

为了保证主端R-P-Y“三连杆”与近端连续体姿态相同，一种方法是保证两者末端在其各自base坐标系旋下描述姿态的转矩阵R相同。 该问题通过代数直接求解的方法不仅计算量大，同时还会存在无解的情况，因此这里引入几何法对其进行求解。首先我们描述一组Fig(  )中的运动：初始坐标系O经过绕y_0旋转θ_3和绕x_1旋转θ_4后形成坐标系O_2；另一方面，初始坐标系经过绕z_0旋转ϕ后形成坐标系O_1^a，再经过绕y_1^a旋转ks后得到坐标系O_2^a，观察两次坐标变换所得坐标系的z轴重合。实际上前者就是描述的三连杆转动yaw和rolling方向上关节对应的坐标变化，而后者是连续体在绳子驱动下偏转后产生的坐标变化，z轴重合代表两者末端朝向一致，不过两个坐标系在x-y轴平面上存在一个偏置(Fig)；

同样的，我们将图(a)中)O2 和 Oa2提取出来，构建新的几何关系。只需要求解上述两个空间夹角，即可得到了映射函数，对于这两个问题均可使用【三余弦定理】，这是一种通过构建投影求解空间夹角的方法，具体的求解过程在附件A中给出。
$$
公式
$$
由此可得最终映射关系：
$$
公式
$$

根据公式(9)推导的函数，我们使用matlab在同一个坐标系下分别绘制主从两端的坐标系Fig6(c)，符合我们的预期，也即z轴重合，x-y平面存在偏执，再结合公式(10-13)求解的x，得到Fig6(d)的结果——两个坐标系完全重合，证明映射的合理性。

## 结论

在这篇文章中，我们提出了一种可以提供主动三角测量性的内窥镜的手术机械臂模型，并设计了一种适配于该类型手术机器人的穿戴式操纵台。在调试的过程中发现末端存在较为显著的震颤，并提出了两种方法改善生理抖动产生的震颤，为了之后主从遥操作做准备，推导了主从之间的映射函数。在后续的工作中会对样机的实体进行迭代，并完成空缺的实验，人机交互的控制策略正在研究中，致力于研发精准且舒适的主端操纵台。

## Reference

[1] Rosin, R. D. (Ed.). (1993). *Minimal access medicine and surgery: principles and techniques* (Vol. 1). Scovill-Paterson.

[2] Gauderer, M. W., Ponsky, J. L., & Izant Jr, R. J. (1980). Gastrostomy without laparotomy: a percutaneous endoscopic technique. *Journal of pediatric surgery*, *15*(6), 872-875.

[3] Rattner, D., & Kalloo, A. (2006). ASGE/SAGES Working Group on natural orifice translumenal endoscopic surgery: October 2005. *Surgical Endoscopy and Other Interventional Techniques*, *20*(2), 329-333.

[4] Giday SA, Kantsevoy SV, Kalloo AN. Principle and history of natural orifice translumenal endoscopic surgery (NOTES). *Minim Invasive Ther Allied Technol*. 2006;15:373–377.

[5] Fuchs, K. H., & Breithaupt, W. (2012). Transgastric small bowel resection with the new multitasking platform EndoSAMURAI™ for natural orifice transluminal endoscopic surgery. *Surgical endoscopy*, *26*, 2281-2287.

[9] Dallemagne, B., & Marescaux, J. (2010). The ANUBIS™ project. *Minimally Invasive Therapy & Allied Technologies*, *19*(5), 257-261.

[10] Kobayashi, T., Lemoine, S., Sugawara, A., Tsuchida, T., Gotoda, T., Oda, I., ... & Kakizoe, T. (2005). A flexible endoscopic surgical system: first report on a conceptual design of the system validated by experiments. *Japanese journal of clinical oncology*, *35*(11), 667-671.

[2-1] Kuniholm, J. F., Buckner, G. D., Nifong, W., & Orrico, M. (2005). Automated knot tying for fixation in minimally invasive, robot-assisted cardiac surgery.

## 一些细节+ 最终调整

* 到底叫console好还是manipulator好

* [ ] 修改tremor部分
  * [ ] 文字修改
  * [ ] 绘制FK模型，编写绘制末端位置的脚本，通过实验收集数据，得到xyz3维度图像
  * [ ] 添加KF后的结果的图像
  * [ ] 
* [x]

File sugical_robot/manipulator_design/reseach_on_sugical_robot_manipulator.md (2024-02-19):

# 手术机器人操作台控制器研究

key word: Surgeon Console Controls, manipulator, telemanipulator

感觉论文的核心还是应该围绕操纵端的设计，说来惭愧，连英文名都说不出来，现在知道了是manipulator（感谢gpt🙏）

### 精读达芬奇

```
Summary: The document is a technical review of the da Vinci surgical telemanipulator, a robotic system used in various surgical specialties. The review analyzes the strengths and weaknesses of the robot design based on published literature and patents. The main findings of the review are that while the da Vinci system facilitates complex surgical operations and has a low malfunction rate, it lacks haptic feedback and collisions between the robotic arms are a major limitation. Accurate positioning of access ports is also essential. The review concludes that knowledge of the technical aspects of the da Vinci robot is important for optimal use and highlights future trends in robot miniaturization and intelligent control design.

Main points:

- The da Vinci surgical telemanipulator is a robotic system used in various surgical specialties.
- The review analyzes the strengths and weaknesses of the robot design based on published literature and patents.
- The system facilitates complex surgical operations and has a low malfunction rate.
- The lack of haptic feedback and collisions between the robotic arms are major limitations.
- Accurate positioning of access ports is essential.
- Knowledge of the technical aspects of the da Vinci robot is important for optimal use.
- Future trends in surgical robotics include robot miniaturization and intelligent control design.
```

### 一篇外骨骼康复手腕万向节设计

锐评：这也能发，那我感觉我写好一点，比他还牛逼，不过可以认真读一下，学习一下它怎么展开写一篇会议论文

[原文](https://ieeexplore.ieee.org/document/6650459)

### 达芬奇三连杆结构

[专利出处](https://patents.google.com/patent/US6364888B1/en?oq=US6364888B1)

专利中把这个结构称为**[wrist gimbal]手腕万向节**；（为什么叫这个？）

专利写的很清楚，但是太啰嗦了，而我重点想研究手腕万向节

### 随口提一嘴：

[手持式同心管手术机器人](https://ieeexplore.ieee.org/abstract/document/9308920)：可以作为

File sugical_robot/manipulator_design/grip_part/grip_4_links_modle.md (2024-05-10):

# grip_4_links_modle

## 手柄四连杆部分力学模型推导

目标：测量操纵者手指提供的压力，并将测量的压力映射到末端手术器械的压力。常规力传感器无法适配这里尺寸较小的结构，尝试通过检测角度，以及力学模型测量指端作用力；

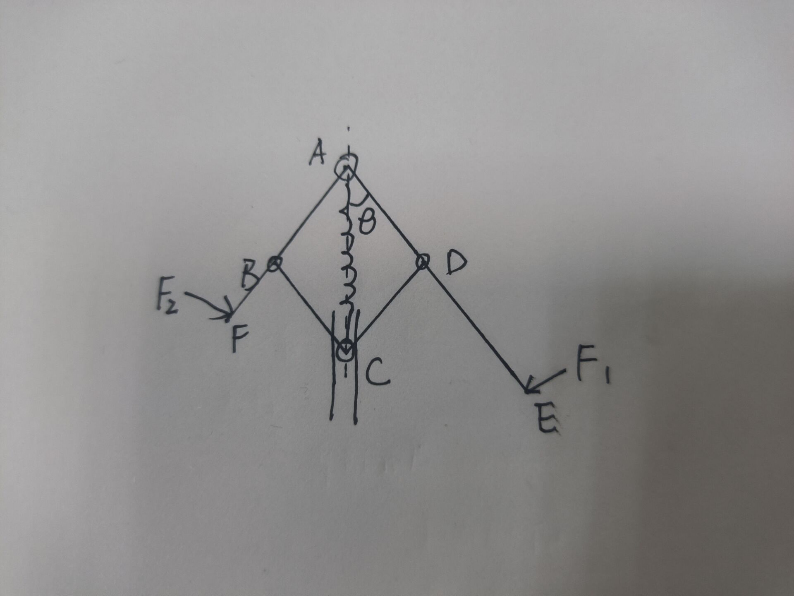
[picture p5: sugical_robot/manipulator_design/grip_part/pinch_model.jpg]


主要任务：推倒四连杆力学模型，找到$F_1, F_2$ 与 $\ang DAC (\theta)$ 之间的关系；

1. 对连杆AE受力分析，根据关于A点力矩平衡，可以得到$F_1$ 与 连杆CD对连杆AE的支持力$F_{N1}$ 之间的关系：
   $$
   F_1 L_1 = F_{N1} l_0 sin(2\theta) \tag{1}
   $$
   同理可得到$F_2$ 与 连杆CD对连杆AE的支持力$F_{N1}$ 之间的关系：
   $$
   F_2 L_2 = F_{N2} l_0 sin(2\theta) \tag{2}
   $$

2. 对连杆CD受力分析，将力分解到x，y两个方向可以得到等式
   $$
   (F_{N1} + F_{N2} ) cos(\theta) = F_{sping} + f \tag{3}\\
   $$

   $$
   (F_{N1} - F_{N2} ) sin(\theta) = F_y \tag{4}
   $$

其中，$F_1, F_2, F_{N1}, F_{N2}, F_y$为未知量，$F_{sping}$ 为拉簧弹力，和$\theta$ 相关，可以通过检测角度获得；4个方程，5个未知数，

.因此有无穷解；对于我们感兴趣的$F_1, F_2$ ，我们只能得到两者之间的关系：
$$
(F_1 L_1 + F_2 L_2 )= 2(F_{spring} + f) l_0 sin(\theta)
$$
这个公式对应的物理含义就是：维持每个位置所需要的力矩；

绘制出$(F_1 L_1 + F_2 L_2 )$ 关于 $\theta$ 的图像

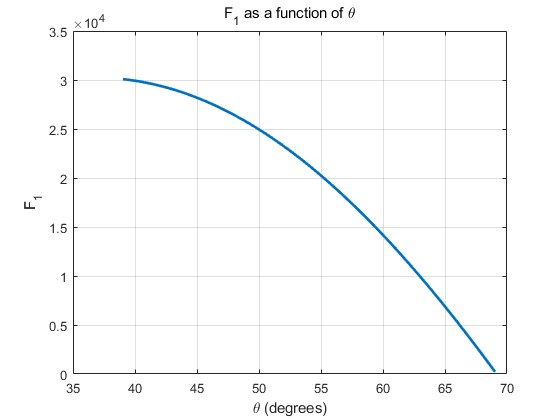
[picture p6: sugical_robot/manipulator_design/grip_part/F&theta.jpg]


## 拉簧选型

通过计算，可以确定弹性系数大致在65左右，且原长为20，半径为3，线粗0.5 => 72.34

注意，线径为0.4时，k = 23.7 (也可以买过来试一下)

有一个问题在于，这是比较理想的条件下，如果引入摩擦力呢对于4连杆部分，摩擦力的主要来源轴承关节、轮子上下表面摩擦，目前感觉不是很大，暂不考虑后面再改进吧；压簧的摩擦力主要来源于平移块与轴之间的摩擦力，

```matlab
% 这个脚本用于计算pinch部分拉簧的弹性系数等参数
L1 = 13.8; 
L2 = 18.5;
l0 = sqrt(L1^2 + L2^2); 

% 弹簧参数确定
l_spring_total = 20;
D_spring = 3;
l_spring = l_spring_total - D_spring; 

% 力矩长度
l1 = 58;
l2 = 33;

theta_i = 120 - rad2deg(atan2(L2,L1));
theta_f = theta_i - 30;
F_max = 250 * (l1 + l2); %tau: g*mm
F_spring_max = F_max / (2 * l0 * sind(theta_f));
delta_x = 2*l0*cosd(theta_f) - l_spring;
k = F_spring_max / delta_x;
disp('拉簧弹性系数：');
disp(k);
```

附加之前扳机设计时的选型：

**扳机拉簧选型：**

| 参数 | 长度(L) | D     | d       | k(g/mm)   |
| ---- | ------- | ----- | ------- | --------- |
|      |         |       |         |           |
|      | 15      | 5     | 0.3     | 4.02      |
|      | 15      | 5     | 0.4     | 19.18     |
|      | **15**  | **5** | **0.5** | **60.01** |
|      | 15      | 4     | 0.5     | 91.11     |
|      | 15      | 3     | 0.5     | 194.44    |
|      | 10      | 3     | 0.4     | 127.45    |
|      | 10      | 3     | 0.5     | 437.5     |

* 手指拉力测试

  轻轻的摁压力大概为300g；稍微用力500g

  300 —— 500 比较合适

以及摁压过程的行程 $x$ = 4;
$$
k = \frac{F}{\Delta x} = 186.864
$$

手指扣拉簧选型

* 经过拉力测试，作用到最远距离所需的压力 F1, F2 (暂定400)分别为，根据推导模型，可以确定在最大型变量时最大的拉力

#### 第二代迭代

之前计算的拉簧弹性系数明显过大实际购买的弹性系数，通过矫正，新的弹性系数确定在32左右

暂定 3 * 0.4 * 20 => k = 28 

### 夹紧机构压簧选型

设计夹紧结构的目的是让操纵者在感觉上能感受到一个明显的变化，知道确定目前是“力控模式”，同时稍微增大拉力程度可以防止施力过大；为了防止把对象捏爆，是不是要加一个**反馈？？？**

需要满足的条件：

* 完全压缩需要小于等于2.5，2.5太小，拓展了一下到5.5
* 夹紧（释放）状态长度为7.5；此时理想的压力为3~5牛

弹簧选型时主要需要确定长度l、直径D、线径d；弹性系数与三者之间的关系是——，反比，正比

通过确定了两组压簧，外径5，线径0.5，长度10/15；

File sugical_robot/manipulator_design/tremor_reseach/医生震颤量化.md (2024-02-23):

## 简介

这篇文章就是设计了一些实验来量化外科手术医生的tremor情况

结果：8-12 Hz范围内的大量振荡——因于生理震颤的增强。医生越做越强。

结论：除了量化了震颤；还建立了传递模型

```
所以这篇文章有看的必要吗；可以作为入门文章，研究一下临床医生震颤的情况；
一句话，我需要知道手术医生手抖到什么情况；如果有解决方案就更好了

```

## Introduction

虽然生理震颤很微弱，但是在不同情况下，或者不同姿势下；震颤的影响会不同的

手术就是一个特例，所以为什么临床手术医生要经过大量的练习做到手不抖，才能做手术（**这里要看更多论文论证**）

* 这篇[论文](https://sci-hub.se/10.1016/j.ncl.2009.04.003)简介又全面的总结了所有震颤，里面也强调了，影响医生的只有physiological tremor
* 

尽管如此，在微创外科手术时，经过[杠杆效应]，**末端的震颤会更加严重**（比如之前穿戴的手术设备，或者专用于微创的）

[提供材料](https://oup.silverchair-cdn.com/oup/backfile/Content_public/Journal/icvts/23/3/10.1093_icvts_ivw150/1/ivw150_Supplementary_Data.zip?Expires=1708564472&Signature=GCM00Gv7KwrgyrZTibInkPciJG6xMZSXOAGPSPsO4Pc1gYUEWIe3uKsTYYS6PdnoDhFFatcO5BW59RvPnff5HlTDEnykRK4SG7-sxaQY59gWd1~iDVoVLI-cC-3TUxkyLlbdEFTwo7w6Dee5k26sWekTZ-v~Sbsp1~zZ4CAYwDq4N1UkFAZ2sbPj3PRDZc6OwAHGW7TaeUiEXLP66asOeSEAZdzx1t1JDYgBG00C44BT3Kl71nMzJp7dSsnK6Rd-O7yCGgXDUCI77vdC1cbo2e6YG9OKsdkcK0AMJ~~cwh3EG5UaIv-2Mn~1VU50~agWKKjgR48DXKxDEgW6dfqI5g__&Key-Pair-Id=APKAIE5G5CRDK6RD3PGA)给了一些解决方法

作者说之前作者过于关注姿态追踪，而忽略了动态动作中的震颤

* application
  * 训练医生？你只是量化，有没有装置
  * 评估医生是否合格
  * 辅助年纪大可能

### Method

介绍了平台的设计，感觉很容易看懂，核心就是两个测量垂直方向力的传感器(为什么单方向的力传感器，可以测量出震动？？？)

### 信号处理

1. 分段
2. 带宽滤波
3. 计算bonferroni系数？
4. 计算关于手术和背景噪声的总结系数？（**没看懂**）
   1. 在8-12 Hz和14-18 Hz的频率范围内分别对频谱功率密度进行积分，分别表示与生理震颤和背景噪声相关的功率（我有点没看懂？）
   2. 与平台相互作用的所有时代贡献的总和。
   3. 总相互作用时间对总和贡献的归一化，并提取平方根
5. 

## 我的总结

读完这篇文章：

1. 他主要的内容是介绍怎么去设计一个实验评价和量化医生在手术时的震动；所以首先你要把他的方法总结出来，然后他做的肯定是很烂，需要改善的

   主要引用的这篇[文章](https://onlinelibrary.wiley.com/doi/abs/10.1002/rcs.1717)：

2. 简介部分提供了一些可以挖掘的信息

   * tremor里面之需要关注physiological tremor；其他医生不会太碰到；
   * 医生到底抖得有多厉害，好像说到现在也就是正常的8-12Hz
   * 文章只做到了竖直方向力的测量，并没有考虑其他方向，而是假设在所有方向振动幅度都一样
   *

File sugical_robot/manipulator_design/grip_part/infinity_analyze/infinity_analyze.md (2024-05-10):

# infinity_analyze

学习了在sw中使用有限元进行分析，首先对装配体整体进行了粗略的分析如下图：





由于装配体比较复杂，存在较大误差， 因此对形变较为明显的零件单独分析

| -           | 目前最大偏置 | 改良结构+尼龙 | 改良结构+金属 |
| ----------- | ------------ | ------------- | ------------- |
| pinch_right | 9            | 1.4 e-1       | 5.7 e-3       |
| pinch_left  | 4.7 e-1      | 2.57 e-2      | 1 e-3         |
|             |              |               |               |
|             |              |               |               |

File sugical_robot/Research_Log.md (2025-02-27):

# Research_Log

* 2025-2-17~2-24

  * 把新一版的结构搭建完（预计2.19~2.21）
  
    新加工的一批零件存在一些问题：
  
    1. 近端和远端均为右旋（大问题）
    2. 有一个远端连杆和左右连接件存在干涉，稍微打磨一下圆角就行了
    3. 远近连杆中间连接零件宽为11.78（小于所需的12.00），长为19.80小于所需的20.00，因此目前装不进去
  
  * 空余时间盯一下专利上传情况（新专利拖一拖）
  
  * 除颤的算法继续尝试
  
  *

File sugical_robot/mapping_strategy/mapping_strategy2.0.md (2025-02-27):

# mapping_strategy2.0

* [x] 整个映射流程，可以用如下过程描述，通过编码器测量五个关节角度信息，得到驱动空间 $\beta_1,\beta_2,\beta_3,\beta_4,\beta_5$

* [x] 将复制的并联机构简化为串联机构，【平面5bar推导】可以得到 主端关节空间  $[\theta_1, d_2, \theta_3, \theta_4, \theta_5]$ 

* [x] 结合【主从关节空间映射】得到 $[D_1, \alpha_2, \Phi_3, \alpha_4,  \Theta_5 ]$

* [x] 目前要做的，是从由常曲率参数$[D_1, \alpha_2, \Phi_3, \alpha_4,  \Theta_5 ]$ 到从端电机驱动空间【具体看论文】；

## 主从关节空间映射

新的机构构型可以简化成下图，对应的坐标系配置：



机构简图中主端的关节空间为 $[\theta_1, d_2, \theta_3, \theta_4, \theta_5]$，从端的关节空间 $[D_1, \alpha_2, \Phi_3, \alpha_4,  \Theta_5 ]$

TODO：**这里从端的简化需要进行证明**（从端不能直接简化成这个）

__________________

之前采取的策略是将关节分为两组解耦，这样虽然简化一些计算，但是由于yaw是由 theta_1, theta_3共同决定，确定了其中一个，另外一个就也确定了，这样会丢失了一个自由度（举个例子：两个一样的平面二连杆做主从映射，目标是保持末端相同，当主端给出一个末端朝向时，从端可以有无数种构型，因为整体有两个自由度，而保持末端朝向只需要一个自由度，这个时候系统是冗余的；但当其中一个被固定时，另一个也固定了）

**总结：之前有5个自由度，但是只干了3个半的事**；因为有两个关节是冗余的，存在多解问题，可以在解空间中，找到一个满足位置约束的解；($\theta_1^t, \theta_2^t$)

所以放弃之前的分部策略，对整体进行分析：（3个姿态向量$\vec{u_R}, \vec{u_P}, \vec{u_Y}$和一个二维位置$x,y$）

对于完全同构的关节，可以从整体中剥离出来—— $\vec{u_P}, \vec{u_Y}$可直接由后面两个两对同构的转动关节独立决定，

于是映射问题就简化成了一个平面的问题：

 $\vec{u_R}$,x,y 由前三个异构自由度决定，并尝试推导新的映射

在满足一个 给定的  $\vec{u_R}$ 后，theta1和theta3仍剩余有自由度，配合d可以得到在平面上位置相等

手术中姿态的重要性大于位置（**这里有点像WBC和NSP的控制策略啊**），因此先保证三个姿态向量一致，也即保证 $\vec{u_R}$一致，此时 theta_1 和 theta_3 会有多个解，如果在这些解中再求出位置的关系（**这个地方我数学不太行**）
$$
\begin{bmatrix}
U_R \\
x_d \\
y_d
\end{bmatrix}
= 
\begin{bmatrix}
\Theta_2 - \Theta_3 \\
f_x(\Theta_2 , \Theta_3) \\
D1 + f_y(\Theta_2,  \Theta_3)
\end{bmatrix}
$$
因为$\Theta_2$和$\Theta_3$是冗余的，一一对应的话，会有一个自由度没有被利用，所以当$\theta_1$和$\theta_3$ 确定时，只需要保证
$$
\theta_1 + \theta_3 = \Theta_1
$$

**TODO**：推导 fx, fy；我是不是可以直接通过其次变换矩阵直接提取？试一下，就不用一个一个推导了

### fx\fz推导

下面是使用matlab计算出来齐次变换矩阵的结果：**感觉关于l的部分有些问题**

f_x:

-d4*(sin(alp4/2)*cos(Phi3)*(cos(alp2/2)^2 - sin(alp2/2)^2) + 2*cos(alp2/2)*cos(alp4/2)*sin(alp2/2)) - l*(cos(alp4/2)*(sin(alp4/2)*cos(Phi3)*(cos(alp2/2)^2 - sin(alp2/2)^2) + 2*cos(alp2/2)*cos(alp4/2)*sin(alp2/2)) + sin(alp4/2)*(cos(alp4/2)*cos(Phi3)*(cos(alp2/2)^2 - sin(alp2/2)^2) - 2*cos(alp2/2)*sin(alp2/2)*sin(alp4/2))) - d2*sin(alp2/2)

f_z:   // 

D1 + d4*(cos(alp4/2)*(cos(alp2/2)^2 - sin(alp2/2)^2) - 2*cos(alp2/2)*sin(alp2/2)*sin(alp4/2)*cos(Phi3)) + d2*cos(alp2/2) + l*(cos(alp4/2)*(cos(alp4/2)*(cos(alp2/2)^2 - sin(alp2/2)^2) - 2*cos(alp2/2)*sin(alp2/2)*sin(alp4/2)*cos(Phi3)) - sin(alp4/2)*(sin(alp4/2)*(cos(alp2/2)^2 - sin(alp2/2)^2) + 2*cos(alp2/2)*cos(alp4/2)*sin(alp2/2)*cos(Phi3)))

$$
p_x = -d_2 \sin \left( \frac{\alpha_2}{2} \right) - d_4( \sin \left( \frac{\alpha_4}{2} \right) \cos(\Phi_3) \cos(\alpha_2) + \cos(\frac{\alpha_4}{2})\sin(\alpha_2)) - l (\sin(\alpha_4) \cos(\Phi_3) \cos(\alpha_2) + \cos(\alpha_4) \sin(\alpha_2) )
 \\

p_z = D_1 + d_2 \cos \left( \frac{\alpha_2}{2} \right) + d_4 \cos(\alpha_2) \cos(\alpha_4) - d_4 \cos(\Phi_3) \sin(\alpha_2) \sin(\alpha_4) + l \cos(\alpha_2) \cos(\alpha_4) - l \cos(\Phi_3) \sin(\alpha_2) \sin(\alpha_4)
$$

```latex
\begin{align*}
p_x &= d_2 \sin \left( \frac{\alpha_2}{2} \right) + d_4 \sin \left( \frac{\alpha_4}{2} \right) \cos(\Phi_3) \cos(\alpha_2) + l \cos(\alpha_4) \cos(\Phi_3) \cos(\alpha_2) + l \sin(\alpha_4) \cos(\alpha_2) \\
p_z &= D_1 + d_2 \cos \left( \frac{\alpha_2}{2} \right) + d_4 \cos(\alpha_2) \cos(\alpha_4) - d_4 \cos(\Phi_3) \sin(\alpha_2) \sin(\alpha_4) + l \cos(\alpha_2) \cos(\alpha_4) - l \cos(\Phi_3) \sin(\alpha_2) \sin(\alpha_4)
\end{align*}
```

但是有一个问题是，我想要的是 $f_x(d_2, \theta_3^e)$ ，而现在得到的是 $f_x(d_2, \Phi_3, \alpha_4)$

好在可以推导出 $\theta_3^e$ 和 $\Phi_3, \alpha_4$ 之间的关系 

不需要推导，也推导不出来，虽然现在fx是由$\Phi_3, \alpha_4$ 表示，但是其实还可以用 $\theta_3, \theta_4$表示（问题就简单很多了），但是这个$\theta_3$还不是$\theta_3^e$，因为$\theta_3^e$等效的是连续体偏转 $\alpha_4$的数值，而只讨论位置的时候末端位置对应的是偏转 $\alpha_4 /2$ ，因此有多引出了一个变量 $\theta_3^f$

两者之间满足的关系是：
$$
c_{\theta_3^e} c_4 = c_{\alpha_2} \\
c_{\theta_3^f} c_4 = c_{\alpha_2/2}
$$
由此可以得到
$$
\theta_3^f = c^{-1}(A * c_{\theta_3^e}) \\
A = \frac{c_{\alpha_2/2}}{c_{\alpha_2}}
$$

$$
P_x = f_x (\alpha_2, \theta_3^f)
$$

______________________

上面推不出来，那就暴力求解把

把fx中三个参数全部用 $\theta_3^e$表示，整理得到一个关于 $\theta_3^e$ 的函数；关于\alpha4和 Phi3的推导，其实之前一直没有完全规定清楚；7-29号重新真正的说清楚

theta3 规定为绕 z3 转动角度，theta4为绕z4转动的角度，两个轴的方向见drawio文件，通俗来说，theta3是偏航左转角度，theta4是俯仰朝上的角度

Phi3规定为器械绕轴转动的角度，具体来说，就是初始的x轴$x_0^s$与转动后的x轴$x_1^s$ 形成的角度，为了满足alpha4 右手定则，规定$x_1^s$与$z_6^s$共轴。

alpha4 规定为转动Phi3后，绕$z_6^s$转动角度，具体轴方向见文件。

由此推导出新的公式：(仅针对theta3,theta4都大于零)
$$
\alpha_2 = A - \theta_3^e\\
\alpha_4 = c^{-1} (c_{\theta_3^e} * c_4) \\
\Phi_3 =  c^{-1}(c_4 s_{\theta_3^e} / s_(\alpha_4)) \\
\Delta x = c^{-1}(c_3 s_{\Phi_3}) + \Phi_3 - \pi/2
$$

将fx单独用 \theta_3^e 表示

最终化简出这样一个结果：
$$
p_x = -d_2 \sin \left( \frac{A - x}{2} \right) - d_4 \left( \sin \left( \frac{\cos^{-1}(c_{x} c_{4})}{2} \right) \cos \left( \cos^{-1} \left( \frac{c_{4} \sin{x}}{\sin(\cos^{-1}(c_{x} c_{4}))} \right) \right) \cos(A - x) + \cos \left( \frac{\cos^{-1}(c_{x} c_{4})}{2} \right) \sin(A - x) \right) - l \left( \sin(\cos^{-1}(c_{x} c_{4})) \cos \left( \cos^{-1} \left( \frac{c_{4} \sin{x}}{\sin(\cos^{-1}(c_{x} c_{4}))} \right) \right) \cos(A - x) + \cos(\cos^{-1}(c_{x} c_{4})) \sin(A - x) \right) \\
\alpha_2 = A - x; \\
       \alpha_4 = c^{-1}(cos(x) * c_4); \\
d_2 = (2s_1 / \alpha_2) * sin(\alpha_2 / 2); \\
d_4 = (2s_2 / \alpha_4) * sin(\alpha_4 / 2);  \\
$$

```latex
p_x = d_2 \sin \left( \frac{A - x}{2} \right) + d_4 \left( \sin \left( \frac{\cos^{-1}(c_{x} c_{4})}{2} \right) \cos \left( \cos^{-1} \left( \frac{c_{4} \sin{x}}{\sin(\cos^{-1}(c_{x} c_{4}))} \right) \right) \cos(A - x) + \cos \left( \frac{\cos^{-1}(c_{x} c_{4})}{2} \right) \sin(A - x) \right) + l \left( \sin(\cos^{-1}(c_{x} c_{4})) \cos \left( \cos^{-1} \left( \frac{c_{4} \sin{x}}{\sin(\cos^{-1}(c_{x} c_{4}))} \right) \right) \cos(A - x) + \cos(\cos^{-1}(c_{x} c_{4})) \sin(A - x) \right)
```

这样一个结果很难有解析解，尝试使用解析法求解 px与theta_3之间的关系，然后构建一个链，需要完成以下任务：

* [x] 编写函数求解这个非线性方程的解（先把fx的方程检查以下，说不定可以简化）；

  * [x] 需要给一组输入值  $\theta_m = [-\pi/6, 10, \pi/3, 0, 0] $，也即给定主端关节，和对应末端的位置；先要把主从大小配合一下，之后再搞缩放 主端长度

* [x] 求解完之后，给出一组主端的关节空间，验证从端是否相同

* [x] 求解D1：用pz _m - pz_s，两者的差值，就是D1，验证代码及其结果在 E:\GitHub\Mac_win\Mac_Win\sugical_robot\mapping_strategy\check_result\check_nolinear_solve.m

* [ ] 要不要做个图像？可能有点费时间，公式以及足够验证其正确性

* [ ] 从驱动空间，到关节空间还没有推导

$f_x$ 是由两段在x轴上的贡献决定

## 主端5bar驱动空间到关节空间



平面五连杆正向运动学主要参考[这里](E:\GitHub\Mac_win\Mac_Win\sugical_robot\mechanical_model\Readme_planar 5 links.md)

这里主要推导一下从主端驱动空间 $[\beta_1, \beta_2, \beta_3]$到关节空间 $[\theta_1, d_2, \theta_3]$的求解过程；

图中u1 和 u5对应 $\beta_1, \beta_2$; 电机角度与初始角度（红色箭头）夹角为$\beta_3$

前两个参数比较好求解：
$$
\theta_1 = \tan^{-1} \frac{l_5/2- x_c}{y_c} \\
d_2 = \sqrt{x_c^2 + y_c^2}
$$
上图中红色箭头为电机的零位，因为电机固定在连杆BC上，所有红色箭头随BC运动而改变，绿色虚线描述坐标系1与坐标系3之间的关系，也即坐标系3的零位，如图所示，五连杆运动时两者之间会出现一个偏差。换而言之，当电机不动，也即$\beta_3$ 保持0时，五连杆的运动会使得红色箭头在绿色虚线坐标系下角度改变，需要人为的减去这个$\Delta \theta$ ；

通过几何关系可以求解：

当电机固定在连杆BC上时（左手）
$$
\theta_3 = \beta - \Delta\theta \\
where,  \Delta\theta =  \theta_1 -  u_2 + 0.2\pi \\
$$
当电机固定在连杆CD上时（右手）
$$
\theta_3 = \beta - \Delta\theta \\
where,  \Delta\theta =  \theta_1 + u_4 - 0.2\pi \\
$$

其中，theta_1 表示五连杆末端点与中心位置O坐标系形成的夹角，theta3表示坐标系3与坐标系2之间的夹角；而α5表示电机实际转动的角度（这里电机实际转动的角度不等于theta3，所以需要推导）

需要简单的验证一下上述结果

通过对两种结构建模，然后

## CCP参数到单元关节参数

根据目前从端连续体逆运动学建模，绳长 $L$ 是和单元关节的参数 $\beta_1, \beta_2$ 关联的，因此还要搭建$\Theta_s$ 到关节参数的映射

关节参数记作$\Beta_s$，
$$
\Beta_s = {\beta_2, \beta_3,\beta_4}
$$
满足如下关系:
$$
\beta_2 = \frac{\alpha_2}{n_p}  \\
\beta_3 = \tan^{-1} (\tan(\alpha_4 / n_d)\cos(\Phi_3) \\
\beta_4 = s^{-1} (\sin {(\alpha_4 / n_d)}  \sin{\Phi_3} )
\\ n_p = 8;
\\ n_d = 6;
$$

### 基于WBC的零空间控制方法

这个方法的核心就是，将需要控制的目标进行分组，分组完以后求解对应的雅可比矩阵（其实没有太搞懂为什么是求雅可比矩阵）

[知乎](https://zhuanlan.zhihu.com/p/164738620)

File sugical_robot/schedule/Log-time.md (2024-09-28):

# Log-time

## Summer_log

目前的工作是新一版的主从控制实现，映射公式只差从常曲率关节空间到驱动空间了

硬件方面；角度都读取，也能够发送，下一步，将映射后的数据发过去，而不是电机驱动空间

* [x] 在c#中实现matlab已有的功能，将其整合到原来的project，有时间优化一下原来project，[参考](https://github.com/SJTU-RoboMaster-Team/Electronic-control-code-specification)
* [x] debug
* [x] 主从通讯调试
* [x] 两种模式==> 增量模式和绝对模式

### 主从映射公式推导

推导了【朝向和位置】满足【直觉映射】的公式，具体内容见

[mapping2.0](E:\GitHub\Mac_win\Mac_Win\sugical_robot\mapping_strategy\mapping_strategy2.0.md)

### 完善主从通讯

[嵌入式调试手册](E:\GitHub\Mac_win\Mac_Win\sugical_robot\EE_control\embedded_testing_log)

```mermaid
graph LR
    A[初始化电机角度] --> B[开始调试]
    B --> C[进入循环]
    C --> D[读取12个关节角度]
    D --> E{判断控制模式}
    E --> F[直觉控制绿灯亮 映射处理]
    E --> G[增量控制简单线性处理]
    F --> H[float转uint8_t 通过CAN发送]
    G --> H[float转uint8_t 通过CAN发送]
    H --> I[继续循环]
    I --> D[循环]
    I --> J[退出条件满足]

```

### 机械结构完善

[机械设计](E:\GitHub\Mac_win\Mac_Win\sugical_robot\mechanical_model\机械结构迭代log)

## Grade 2-up

上个学期大致完成了机械结构的搭建，同时在暑假完成了映射公式的推导，但是映射结果只用matlab进行了简单的数字验证，存在如下问题：

* 可能存在死区
* 结果不够直观

下一步计划是通过Qt搭建一个可视化界面，简易版是实时显示末端点（Position）+ 箭头(Orientation) 变换

[GUI传动什么](E:\Qt_Project\SR_Gui\SR_Gui.md)

### 震颤研究

因为老板不让学习Qt，因此GUI搭建计划被中断，只能之后晚上抽时间学一下了。

[tremor_research](E:\GitHub\Mac_win\Mac_Win\sugical_robot\tremor_research\tremor_in_surgical_robot.md)

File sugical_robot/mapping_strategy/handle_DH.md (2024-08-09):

## DH建模方法复习：

* 坐标系配置需要满足条件：
  * 坐标轴 $x_{i+1}$ 垂直于坐标轴$z_i$
  * 坐标轴 $x_{i+1}$ 与坐标轴$z_i$相交
* 四个主要参数
  *  **a** 是轴 $z_i$ 与 $z_{i+1}$之间沿轴线 $x_{i+1}$ 之间的距离
  *  **$\alpha$** 是垂直于 $x_{i+1}$ 平面测得两个z轴之间的夹角，正向从 i 到 i+1
  *  **d** 是从坐标系i原点o到轴线 $x_{i+1}$与$z_i$交点 o' 之间的距离
  *  **$\theta$** 是垂直于$z_i$平面从两个x轴之间的夹角，同样遵循从低到高为＋

| link | $a_i$  | $\alpha_i$ | $d_i$                                 | $\theta_i$                                |
| ---- | ------ | ---------- | ------------------------------------- | ----------------------------------------- |
| base | 0      | -90        | 0                                     | 90                                        |
| 1    | 0      | 90         | <font color = red>**$d_1^*$**</font > | 0                                         |
| 2    | a_2    | 0          | d_2                                   | <font color = red>$90+\theta_2^*$</font>  |
| t2   | 0      | 90         | d_{t2}                                | <font color = red>$\theta_3^*$</font>     |
| 3    | 0      | 0          | d_3                                   | 90                                        |
| t3   | a_{t3} | -90        | 0                                     | <font color = red>$-90+\theta_4^*$</font> |
| 4    | a_4    | -90        | 0                                     | -90                                       |
| 5    | 0      | 0          | -d_5                                  | <font color = red>$\theta_5^*$</font>     |

**$d_1^*$** : 0-130mm 

a_2 = 218.55mm  ;  d_2 = 60.1mm

d_{t2} = 165mm

d_3 = 90mm

a_{t3} = 155//为什么这两个不相等？

a_4 = 90mm 

d_5 = 15

添加extended系里坐标轴后的DH表：

为了方便绘图，让整体绕世界坐标系x轴旋转90°

相当于多添加一个关节

| link | $a_i$  | $\alpha_i$ | $d_i$                                 | $\theta_i$                                | 对应从端坐标系 |
| ---- | ------ | ---------- | ------------------------------------- | ----------------------------------------- | -------------- |
| base | 0      | -90        | 0                                     | 90                                        |                |
| 1    | 0      | 90         | <font color = red>**$d_1^*$**</font > | 0                                         |                |
| e0   | 0      | -90        | de0 = d_2                             | <font color = red>$\theta_2^*$</font>     |                |
| e1   | 0      | 0          | de1 = a2                              | 0                                         | $z_0$          |
| 2    | 0      | 90         | 0                                     | 0                                         |                |
| t2   | 0      | 90         | d_{t2}                                | <font color = red>$90+\theta_3^*$</font>  |                |
| 3    | 0      | 0          | d_3                                   | 90                                        |                |
| t3   | a_{t3} | -90        | 0                                     | <font color = red>$-90+\theta_4^*$</font> |                |
| 4    | -a_4   | -90        | 0                                     | -90                                       | $z_4$          |
| 5    | 0      | 0          | -d_5                                  | <font color = red>$\theta_5^*$</font>     | $z_5$          |

借助matlab计算得到二连杆部分（控制偏转）的齐次变换矩阵如下：

2-27结果：
$$
\begin{bmatrix} -sin(3),& -cos(3)*sin(4), & cos(3)*cos(4),&  -a4*sin(3) + d3*sin(3) + at3*cos(3)*cos(4)\\
cos(3),&  -sin(3)*sin(4),& cos(4)*sin(3),&  at3*cos(4)*sin(3) - d3*cos(3) + a4*cos(3)\\
         0,&   cos(4),&      sin(4),&                           dt2 + at3*sin(4) \\
        0,&                      0,&                       0,&                                                             1\end{bmatrix}
$$

---
3-2日修改了坐标系配置，计算新的结果如下：
$$
\begin{bmatrix} c_3,& -s_3*s_4, & -c_4*c_3,&  a_4*c_3 + d_3*c_3 - a_{t3}*s_3*c_4\\
0,&  c_4,& -s_4,&  a_{t3}*s_4*s_3 - d_{t2}\\
         s_3,&   c_3*s_4,&     c_3*c_4,&                     a_4*s_3 + d_3*s_3 + a_{t3}*c_3*c_4       \\
        0,&                      0,&                       0,&                                                             1\end{bmatrix}
$$

___

二连杆+小臂偏转部分（整体控制朝向）的齐次变换矩阵：
$$
[cos(2 + 3), -sin(2 + 3)*sin(4), -sin(2 + 3)*cos(4), a4*cos(2 + 3) + d3*cos(2 + 3) - a2*sin(2) - at3*sin(2 + 3)*cos(4)] \\
[sin(2 + 3),  cos(2 + 3)*sin(4),  cos(2 + 3)*cos(4), a4*sin(2 + 3) + d3*sin(2 + 3) + a2*cos(2) + at3*cos(2 + 3)*cos(4)] \\
[                   0,                      -cos(4),                       sin(4),                                                                                d2 + dt2 + at3*sin(4)] \\
[                   0,                                 0,                                  0, 1]
$$

$$
\begin{bmatrix}   c_4*s_5,&  c_4*c_5,   &    s_4,&    d_2 + d_{t2} + a_{t3}*s_4 + d_5*s_4 \\
s_{2 +3}*s_4*s_5 - c_{2 +3}*c_5,&  c_{2 + 3}*s_5 + s_{2 + 3}*c_5*s_4, & -s_{2 + 3}*c_4, &     d_3*c_{2 + 3} - a_4*c_{2 + 3} - a_2*s_2 - a_{t3}*s_{2 + 3}*c_4 - d_5*s_{2 +3}*c_4\\
- s_{2 + 3}*c_5 - c_{2 + 3}*s_4*s_5, & s_{2 + 3}*s_5 - c_{2 + 3}*c_5*s_4,&  c_{2 + 3}*c_4,& d_1 - a_4*s_{2 + 3} + d_3*s_{2 + 3} + a_2*c_2 + a_{t3}*c_{2 + 3}*c_4 + d_5*c_{2 + 3}*c_4\\
 0,& 0, & 0, &1\end{bmatrix}
$$

## 连续体

DH-table 

3-5日发现左右手坐标系建模错误，因此需要对下DH参数表进行修改：

| link | $a_i$ | $\alpha_i$ |  $d_i$  |  $\theta_i$   |
| :--: | :---: | :--------: | :-----: | :-----------: |
|  1   |   0   |   -pi/2    |    0    | $\theta_1 ^*$ |
|  2   |   0   |    pi/2    |    0    | $\theta_2^*$  |
|  3   |   0   |   -pi/2    | $d_3^*$ |       0       |
|  4   |   0   |    pi/2    |    0    | $\theta_4^*$  |
|  5   |   0   |     0      |    0    | $\theta_5^*$  |

$$
\begin{cases}
\theta_1 = -\theta_5 = \phi \\
\theta_2 = \theta_4 = \frac{ks}{2} \\
d_3 = \frac{2}{k} sin(\frac{ks}{2})
\end{cases}
$$

## 主端驱动空间到从端构型空间映射：

根据约束一中关系，我们需要根据主端手指朝向，计算该朝向下齐次变换中的旋转矩阵，由于主从两端朝向相同，因此在初始末端坐标系和世界坐标系相同的情况下，主从两边旋转矩阵部分应该相同。由于最终的旋转矩阵只有三个偏转关节决定，因此只需要考虑从坐标系$O_1$ 与 坐标系$O_4$ 之间的关系。其中坐标$O_1$ 对应的小臂偏转与手腕偏转完全独立，因此可以分开分析，以下推导主端关节变量$[\theta_2, \theta_3, \theta_4]^T$ 与 从端两端连续体变量$[k_1, s_1, \phi_2, k_2, s_2]^T$上述主端变量如图__ 所示，其中从端变量$k_1, s_1$ 分别表示近端连续体曲率和长度，由于近端只有在一个平面的自由度，因此对应的偏转角度为0，同理后面三个参数分别对应远端连续体偏转角度，曲率和长度。

#### 小臂偏转关节与近端连续体：

单独考虑小臂只有一个旋转过程，对应的旋转矩阵为$Rot (\hat{Z_1},\theta_2) $ ，
$$
Rot (\hat{Z_1},\theta_2) = \begin{bmatrix} c_{\theta_2} & -s_{\theta_2} & 0\\
s_{\theta_2} & c_{\theta_2} & 0 \\
0& 0 &1\end{bmatrix}
$$
根据前文中连续体运动学建模结构，近端平面连续体齐次变化矩阵中的旋转矩阵$R_{s1}$
$$
R_{s1} =\begin{bmatrix}c_{k_1s_1} & 0 & -s_{k_1s_1}\\
0& 1 &0 \\
s_{k_1s_1} &0& c_{k_1s_1} 
\end{bmatrix}
$$

由于两者坐标系刚好差$pi/2$，因此只需满足
$$
k_1s_1 = \theta_2
$$

#### 手腕偏转关节与远端连续体：

为了使得初始状态下末端与起始段坐标系关系一致，在现有坐标系基础上添加两个额外坐标系如下图：

**图片**

列出新坐标系对应的DH表：

| link | $a_i$  | $\alpha_i$ | $d_i$                                 | $\theta_i$                                | 对应从端坐标系 |
| ---- | ------ | ---------- | ------------------------------------- | ----------------------------------------- | -------------- |
| 1    | 0      | 90         | <font color = red>**$d_1^*$**</font > | 90                                        |                |
| e0   | 0      | -90        | de0                                   | <font color = red>$\theta_2^*$</font>     |                |
| e1   | 0      | 0          | de1                                   | 0                                         | $z_0$          |
| 2    | 0      | 90         | 0                                     | 0                                         |                |
| t2   | 0      | 90         | d_{t2}                                | <font color = red>$90+\theta_3^*$</font>  |                |
| 3    | 0      | 0          | d_3                                   | 90                                        |                |
| t3   | a_{t3} | -90        | 0                                     | <font color = red>$-90+\theta_4^*$</font> |                |
| 4    | a_4    | -90        | 0                                     | -90                                       | $z_4$          |
| 5    | 0      | 0          | -d_5                                  | <font color = red>$\theta_5^*$</font>     | $z_5$          |

计算坐标系$O_4$ 在坐标系$O_{e1}$ 下的齐次变换矩阵 $ ^{e1} _4T$
$$
^{e1} _4T =\begin{bmatrix} c_3,& -s_3*s_4, & -c_4*c_3,&  a_4*c_3 + d_3*c_3 - a_{t3}*s_3*c_4\\
0,&  c_4,& -s_4,&  a_{t3}*s_4*s_3 - d_{t2}\\
         s_3,&   c_3*s_4,&     c_3*c_4,&                     a_4*s_3 + d_3*s_3 + a_{t3}*c_3*c_4       \\
        0,&                      0,&                       0,&                                                             1\end{bmatrix}
$$
同样根据之前连续体模型，可以得到远端连续体末端坐标系$O_p$与起事端坐标系$O_q$ 之间的齐次变化矩阵 $ ^q_pT$如下:
$$
^q_pT = \begin{bmatrix}c^2_{\phi2}*(c_{k_2,s_2}-1) +1,& s_{\phi_2}c_{\phi_2}(c_{k_2s_2}-1),& -s_{k_2s_2}*c_{\phi2},& -d_3*s_{\frac{k_2s_2}{2}}*c_{\phi2} \\
(c_{k_2,s_2} -1)*s_{\phi_2}*c_{\phi_2}, & c^2_{\phi2}(1-c_{k_2s_2}) + c_{k_2s_2}, &-s_{k_2s_2}*s_{\phi_2},& -d_3*s_{\frac{k_2s_2}{2}}*s_{\phi_2} \\
       c_{\phi_2} s_{k_2s_2},  &      s_{\phi_2}s_{k_2s_2},             &           c_{k_2,s_2},    &      d_3*c_{k_2s_2/2}\\
              0,    &    0,            &                  0,          &           1 \end{bmatrix}
$$

通过观察$^{e1} _4T$ 和  $ ^q_pT$ ，其中旋转矩阵部分无法保证恒相等。为了解决该问题，对主从两端坐标系变换进行分析：为了便于理解，以下用欧拉角的方式对旋转变换进行描述。

 two_links_axis_rotationcontinuum_rotation

<font color = red>以下全为错误结论</font>

______________________________

由上图可以看出，主端二连杆的运动是由绕$y_m$轴偏航($R_{y_m,\theta_3}$)和 绕$x^1_m$轴俯仰$(R_{x^1_m,\theta_4})$ 组合而成；而连续体的坐标变换是由绕$z_a$轴滚动$(R_{z_a, \phi_2})$ 后绕$y^2_a$ 偏航$(R_{y^2_a,k_2s_2})$ ，再绕$z^2_a$ 滚动$(R_{z^2_a,-\phi})$ 。通过上述分析，可以知道主端只有俯仰和偏航的旋转，而从端只有滚动和偏航的旋转，两者无法等效。这里提出的解决方法是将主端的两次旋转分作两步分析，主端单独的偏航($R_{y_m,\theta_3}$)可以借助从端偏航$(R_{y^1_a,\theta_3})$描述，而主端的俯仰$(R_{x^1_m,\theta_4})$ 可以通过从端绕$z_a$滚动90°$(R_{z_a, \frac{\pi}{2}})$后再绕$y^2_a$ 偏航$\theta_4$ $y^2_a$ 偏航$(R_{y^2_a,\theta_4})$。从端需要进行两次坐标变换才能实现与主端同步，两次变换的参数需要满足以下关系：
$$
\begin{cases}
\begin{cases}
\phi^1_{2} = 0\\
k^1_2s_2 = \theta_3
\end{cases} \\

\begin{cases}
\phi^2_{2} = \frac{\pi}{2}\\
k^2_2s_2 = \theta_4
\end{cases}
\end{cases}
$$
**正负号规定：所有旋转角度正负号均遵守右手定则；**

注：由于曲率只能是正数，因此当$\theta_3,\theta_4$ 为负数时，$\phi^1_{2} = \pi, \phi^2_{2} = -\pi/2$

经过反思，上述“两步走”的方法中，第二次是在第一次的基础上进行了，也就是第二次旋转矩阵$R_1 = (R_{z_a, \frac{\pi}{2}})* (R_{y^2_a,\theta_4}) $右乘$R_2 = (R_{y^1_a,\theta_3})$ ，这样等价于两个串联单自由度连续体共同作用的结果，而实际上，我们这里只讨论一个具有双自由度的连续体，因此上述结论错误。

_______________________

经过重新分析，我提出了两种解决方法：

* “两步走”的思路应该是可行的，但是两步应该都是在连续体的世界坐标系$O_a$下进行变换，这个也是我先用第二种思路做出来后才想清楚的，结果和思路二一样，但是不如思路二简洁，这里不多做描述
* 另一个思路是末端朝向相同的硬约束其实只有z轴重合，x,y可以通过后续绕z轴的旋转来调整

<<<<<<< HEAD

##### 思路二

下图描述了二连杆先绕$y_0$ 旋转$\theta_3$后，再绕$x_1$ 旋转$\theta_4$后得到最终二连杆末端坐标系$O_2$的过程，观察下图可以发现，该结果同样可也通过先绕$z_0$旋转$\phi$ 角度后得到坐标系$O^a_1$，再绕$y^a_1$ 旋转$ks$得到坐标系$O^a_2$ 该坐标系满足于坐标系$O_2$z轴同向，但是x-y存在一个偏置需要弥补；这里主要的问题是如何借助几何关系，根据已知的$\theta_3,\theta_3$ 求解 $\phi, ks$

[三余弦定理](https://zhuanlan.zhihu.com/p/401766934)描述的是空间中满足投影关系的三个角满足以下关系:


$$
cos \beta = cos \alpha * cos \gamma
$$
借助图中两组投影关系：$z_2$在$z_o Ox_o$上的投影为$z_1$，在$y_o Ox_o$上的投影为$OA$

三余弦组合1:$z_0-z_1-z_2$
$$
cos(ks) = cos(\theta_3) * cos(\theta_4) 
$$
三余弦组合2：$x_0-z_1-z_2$
$$
cos(z_20x_0) = cos(\frac{pi}{2} - \theta_3) * cos(\theta_4)
$$
三余弦组合3：$OA-x_0-z_2$
$$
cos(z_20x_0) = cos(\phi) * cos(\frac{pi}{2} - ks)
$$
由等式$(1),(2),(3)$联立求解可得
$$
ks = cos^{-1} (c_3 c_4) \\
\phi = cos^{-1} (\frac{c_4 s_3}{s_{ks}}) 
$$
使用matlab验证上述结论(4):





其中绿色坐标系为世界坐标系，红色坐标系为主端二连杆末端朝向，蓝色坐标系为连续体末端朝向，通过可视化坐标系变换可以验证该公式可以满足z轴同一朝向，但是x-y平面存在一个偏置。通过寻找新的几何关系：

_____

**这个部分的公式也求出来了，但是验证不正确，我暂时找不到问题出在哪里？**

____

由于上述方法采用的几何法，公式中多处出现反三角函数，而反三角函数无法求解出负角度，因此还需要人为的添加正负变换，通过总结，正负号满足以下结果：

| $\theta_4 < 0$ | $\theta_4 > 0$ |
| ---- | -------------- |
| $\begin{cases} \phi = \phi \\ \Delta x = \Delta x  \end{cases}$ | $\begin{cases} \phi = -\phi \\ \Delta x = -\Delta x  \end{cases}$ |

由此可以得到主端驱动空间 $AS_{master} = [d_1, \theta_2,\theta_3,\theta_4,\theta_5]^T$ 到从端构型空间 $CS_{slave} = [D_1, ks_1,ks_2, \phi_2, \Theta_5]^T $之间的映射关系：

**公式**

### 从端构型空间与驱动空间映射

=======
由此可以得到主端驱动空间 $AS_{master} = [d_1, \theta_2,\theta_3,\theta_4,\theta_5]^T$ 到从端构型空间 $CS_{slave} = [D_1, \phi_1, k_1, \phi^1_2, k^1_2,\phi^2_2, k^2_2, \Theta_5]^T $之间映射关系：
$$
\left[ \begin{matrix}
   x \\
   y \\
   1 
  \end{matrix}
  \right] = \left[
 \begin{matrix}
   f & 0 & O_x\\
   0 & f & O_y\\
   0 & 0 & 1
  \end{matrix}
  \right] \left[
 \begin{matrix}
   \bar{x} \\
   \bar{y} \\
   z
  \end{matrix}
  \right] \tag{1}
$$

## 从端构型空间到驱动空间映射：

目前通过前一步计算得到了从端手术臂的构型信息，但是在驱动时只能直接控制手术臂的驱动空间，在该项目中，末端的柔性手术臂是使用线缆的方式驱动，因此驱动空间的变量为每个关节对应的绳长，需要通过推导绳长与构型之间的映射关系才能通过驱动线缆得到预期的构型。
$$
\begin{cases} s(q) = \frac{l_1 +l_2 +l_3 +l_4  }{4} \\
\phi(q) = tan^-1(\frac{l_4 - l_2}{l_3 - l_1}) \\
k(1) = \frac{(l_1 -  3l_2 + l_3 + l_4)\sqrt{(l_4 - l_2)^2 + (l_3 - l_1)^2})}{d(l_1 +l_2 +l_3 +l_4)(L4-l2)} \\
l_1 + l_3 = l_2 + l_4 = 2l_0 \\
\end{cases}
$$

$$
^{i-1} _iT_d = \begin{bmatrix} 1 & 0 & 0 & 0 \\
0 & cos(\beta_{dx}) & -sin(\beta_{dx}) & -l_{dt}sin(\beta_{dx}) \\
0 & -sin(\beta_{dx}) & cos(\beta_{dx}) & l_{dt}cos(\beta_{dx}) \\
 0 & 0 & 0 &1
\end{bmatrix}
$$

$$
T_y = ^{i-1} _iT_d = \begin{bmatrix}
cos(\beta_{sy}) &0 &  sin(\beta_{sy}) & l_{dt}sin(\beta_{sy}) \\
 0 & 1 & 0 & 0 \\
-sin(\beta_{sy}) &0 &  cos(\beta_{sy}) & l_{dt}cos(\beta_{sy}) \\
 0 & 0 & 0 &1
\end{bmatrix}
$$

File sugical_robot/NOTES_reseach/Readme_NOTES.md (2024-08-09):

# NOTES手术机器人调研

## NOTES定义

[祖师爷](https://link.springer.com/article/10.1007/s00464-005-3006-0)：最初NOTES的定义：

NOTES，即Natural Orifice Translumenal Endoscopic Surgery（自然腔道内镜手术），是一种新兴的微创手术技术。它**通过身体的自然腔道（如口腔、肛门或阴道）进入体内**，进行手术操作，而不是通过传统的皮肤切口。这种手术方式允许医生在不切开皮肤的情况下，通过内镜技术进入腹腔或胸腔进行手术。NOTES技术包括了组织切除和修复，其目标是减少手术创伤，加快病人的恢复速度，并改善术后的美观效果。

优点：

- **患者恢复更快**：由于NOTES避免了皮肤切口，因此可以减少手术创伤，使得病人的恢复过程更加迅速。
- **减少疼痛**：与传统的腹腔镜手术相比，NOTES可能进一步减少术后疼痛，因为皮肤切口是疼痛的一个主要来源。
- **更好的美容效果**：没有皮肤切口意味着术后不会留下疤痕，对于追求美观的患者来说是一个重要的优势。
- **潜在的更广泛的应用**：NOTES可能使得一些复杂的手术程序变得更加微创，甚至可能实现目前腹腔镜手术难以或无法完成的手术。
- **技术进步的推动**：随着内镜技术和相关设备的进步，NOTES提供了一种新的治疗手段，使得手术更加精准和安全。

[微创柔性机器人概述](https://ieeexplore.ieee.org/abstract/document/9226520)

记录这个文档的目的是，调研目前已有的经自然腔道手术机器人；

总结它们的特点（优缺点），应用于哪些手术

明确我们手术场景，为后续研究指明方向、

NOTES手术机器人需要有：可操作性、独立的摄像头铰接、三角测量和直观的控制

一般的NOTES手术机器人具有以下自由度：



## 总结

	写这个文档的目的是为了找到基于内窥镜的双通道手术人的应用场景，也即最适配双通道的手术，看了一些文章，其中医学类更偏向于介绍病理，关于手术机器人的文章更偏向于机器人的设计，而没有具体的应用场景。

	虽然想找到符合“内窥镜和微创手术”都不好做的手术，但是可能对具体的病不太了解，更不懂它手术的过程，因此至今没有找到符合上述条件的；目前调整策略，首先收集常见的消化道疾病，然后标出其中可以用内窥镜进行治疗的疾病，因为凡是内窥镜能够完成的，双通道肯定能向下兼容，且完成的效果更好。然后在这些疾病中寻找符合上述条件的疾病

**根据KIMI提供的资料：**

### 可以使用内窥镜治疗的手术：

1. **早期胃肠道肿瘤**：内窥镜下黏膜切除术（EMR）或内窥镜下黏膜剥离术（ESD）可用于早期胃癌或肠癌的治疗。 1
2. **胃肠道息肉切除**：内窥镜下可以切除大部分的息肉。 1
3. **胃食管反流病（GERD）**：部分患者可能接受内窥镜下的抗反流手术，如Stretta程序。2
4. **胆道梗阻**：内窥镜逆行胰胆管造影（ERCP）可用于清除胆道结石或放置支架。1
5. **食管狭窄**：内窥镜下扩张术或放置支架。 1
6. **Barrett's食管**：对于部分高级别异型增生，内窥镜下消融治疗可能适用。1
7. **痔疮**：内窥镜下硬化疗法或橡皮筋结扎术。0

### 内窥镜无法治疗的手术：

1. **进展期胃肠道肿瘤**：需要开放手术或腹腔镜手术进行肿瘤切除。0
2. **肠梗阻**：可能需要手术解除梗阻，特别是由疝气、肿瘤或其他原因引起的机械性梗阻。0
3. **炎症性肠病**（如克罗恩病或溃疡性结肠炎）：在药物治疗无效或出现严重并发症时可能需要手术。0
4. **胆结石和胆囊炎**：通常需要腹腔镜胆囊切除术。0
5. **胰腺炎**（慢性或反复发作）：可能需要手术引流或切除部分胰腺。0
6. **胰腺肿瘤**：需要手术切除肿瘤。0
7. **食管穿孔或破裂**：需要紧急开放手术修复。2
8. **胃和十二指肠溃疡**：在药物治疗无效或出现并发症时可能需要手术。2
9. **腹壁疝**：如腹股沟疝、脐疝等，通常需要手术修复。0
10. **肛门直肠疾病**：如严重的痔疮、肛瘘等可能需要开放手术。0
11. **消化道瘘管**：复杂的瘘管可能需要手术修复。0
12. **先天性消化道畸形**：如先天性巨结肠，需要手术矫正。0
13. **肥胖症**：在极端肥胖且其他治疗方法无效时，可能需要减肥手术，如胃束带术或胃旁路术。0

以下是根据是否可以通过内镜手术治疗来分类的这些手术：

### 可以通过内镜手术治疗的疾病

1. **贲门失弛缓症**：1
   - **内镜手术**：经口内镜肌切开术（POEM）。

2. **消化性溃疡病（并发症如出血）**：1
   - **内镜手术**：内镜止血治疗（用于急性出血）。

3. **结直肠癌（早期阶段或息肉）**：
   - **内镜手术**：息肉切除术（内镜下切除息肉）、内镜黏膜切除术（EMR）。

4. **食管癌（早期阶段）**：
   - **内镜手术**：内镜黏膜切除术（EMR）。

### 不能通过内镜手术治疗的疾病

1. **阑尾炎**：0
   - **手术治疗**：阑尾切除术。
   - **手术类型**：开放手术或腹腔镜手术。

2. **胆结石（胆石症）**：0
   - **手术治疗**：胆囊切除术。
   - **手术类型**：腹腔镜胆囊切除术或开放胆囊切除术。

3. **疝气（腹股沟疝、食管裂孔疝等）**：0
   - **手术治疗**：疝修补手术。
   - **手术类型**：开放手术或腹腔镜手术。

4. **憩室炎（复杂病例）**：0
   - **手术治疗**：肠段切除术。
   - **手术类型**：开放手术或腹腔镜手术。

5. **结直肠癌（晚期或复杂病例）**：0
   - **手术治疗**：结肠切除术、直肠切除术。
   - **手术类型**：开放手术、腹腔镜手术或机器人手术。

6. **炎症性肠病（IBD）（严重病例）**：0
   - **手术治疗**：切除病变肠段、结肠切除术、直肠结肠切除术。
   - **手术类型**：开放手术或腹腔镜手术。

7. **胃食管反流病（GERD）（严重、顽固性病例）**：2
   - **手术治疗**：胃底折叠术。
   - **手术类型**：腹腔镜手术或开放手术。

8. **消化性溃疡病（并发症如穿孔）**：2
   - **手术治疗**：修补穿孔、部分胃切除术、迷走神经切断术。
   - **手术类型**：开放手术或腹腔镜手术。

9. **食管癌（晚期病例）**：
   - **手术治疗**：食管切除术。
   - **手术类型**：开放手术、微创食管切除术。

这些分类展示了哪些疾病可以通过内镜手术治疗，哪些需要更传统的开放或腹腔镜手术。

可以治疗：

* **贲门失弛缓症**： —— POEM
* 息肉 —— 息肉切除术
* 早期胃肠道肿瘤  —— 内窥镜下黏膜切除术（EMR）或内窥镜下黏膜剥离术（ESD）
* 早期Barrett's食管 / 早期食管癌—— 通过（EMR）和内窥镜下消融可以治疗
* 消化道溃疡出血——止血夹
* **胆道梗阻**——内窥镜逆行胰胆管造影（ERCP）可用于清除胆道结石或放置支架。
* 一篇论文中提到的IDEA使用内窥镜对自然腔通道进行化疗

这些中目前已知只有息肉切除是广泛应用于临床中，需要查找EMR和ESD的应用程度，如果比较低，侧面就能说明这个单纯的内窥镜对这个治疗是有一定难度的，，有【硕士论文】提出EMR和ESD手术时剥离的黏膜容易粘连；同样的道理是不是可以应用在POEM术上面？胆道梗阻因为过于狭窄，不适合

可能可以：（重点了解GERD的手术过程）

* [胃食管反流病](https://www.youtube.com/watch?v=zh-9RaSCMxQ)（GERD）：与贲门失弛缓症相反，贲门肌肉无法提供约束力使得胃酸倒流，
  * [胃底折叠术](https://www.youtube.com/watch?v=9bnIuKiHdDE)（需要借助开放手术/MIS将胃和食道相连接部分的肌肉进行折叠，包裹食道，以产生收缩能力），显然这个我们做不了
  * 经口无切口胃底折叠术 (TIF)
  * 这个视频总结了[6种方法](https://www.youtube.com/watch?v=tIm0aLB2n28)
* 食管穿孔或破裂
* 胃溃疡

不可以：

* 进展期胃肠道肿瘤——需要手术切除
* 肠梗阻：机械性梗阻，如疝气、肿瘤更原因，需要开放手术
* 胆结石和胆囊炎
* **胰腺肿瘤**：需要手术切除肿瘤
* 食管穿孔或破裂
* 胃和十二指肠溃疡
* 腹壁疝
* 

消化道中无法通过内窥镜直接治疗的疾病通常需要涉及到器官或大规模组织的摘除或其他操作，如：阑尾炎、胆结石、进展期胃肠道肿瘤、肠梗阻、胰腺肿瘤、腹壁疝、炎症性肠病、食管癌等，必须借助开放手术的外力或者微创手术。但是对于部分手术，目前主流的方式是开放手术、微创手术，内窥镜搭载双臂机器人后有替代的潜力，比如对于胃食道反流术，

以上都是在消化道内部进行的手术，在文章中成为direct NOTES，还有一种叫distant NOTES，需要通过“invade”一个健康的器官到达另外一个器官，比如通过肠道造孔切除阑尾、子宫造孔切除胆；

## 从MIS角度来看

目前讨论了在intraluminal上的应用，需要继续查询MIS在腹腔内不能完成，而NOTES能够比较好完成的手术

MIS 主要的缺陷：

* 视野十分受限；
* 

## 用在什么手术

目前已经明确的事情是，内窥镜可以到达狭窄的地方（消化道、呼吸道、泌尿道：食管、胃、结肠、输尿管、支气管和动脉），但是比较费劲的手术（**就是要重点找这个**），内窥镜做不了；

| -                                                            | 内窥镜               | 内窥镜手术机器人 | 微创 | 备注                                                         |
| ------------------------------------------------------------ | -------------------- | ---------------- | ---- | ------------------------------------------------------------ |
| [esophagectomy(食道切除术)](https://www.youtube.com/watch?v=pnbknL5WENk) | 否                   | ？               | 勉强 | 需要切的部分太大了，根据[BBC提供的食道手术切除视频](https://www.youtube.com/watch?v=KnxnJzAzTaY)，首先会用内窥镜检查内部，最后用微创手术设备从外部检查，最终进行开放手术，可见最终还是需要开放手术，可能早期能使用MIS；[动画演示](https://www.youtube.com/watch?v=NeUoxmEOnAM) |
| Achalasia(贲门失弛缓症)                                      | 是                   | 是               | 可以 | 手术的原理是，切除贲门的一块肌肉，使用开放手术创伤过大，MIS需要从外部切开，且难以应对靠近背部的肌肉；目前主要是用内窥镜治疗 |
| [内镜黏膜切除术 (EMR)](https://www.youtube.com/watch?v=AI5zjDag1-w) | 是                   | 是               | 否   |                                                              |
| [内镜黏膜下剥离术 (ESD)](https://www.youtube.com/watch?v=kngn2NY6gC8) | 只适用于小型肿瘤切除 | 是               | 否   |                                                              |
| 胃部肿瘤晚期                                                 | 否                   | 否               | 是   |                                                              |
| [Tracheal Stenosis 气管狭窄堵塞](https://www.youtube.com/watch?v=ps5OLq9JfFA) |                      |                  |      | 与食道狭窄很像，但是开放手术的步骤更多，这种管道切除术，有没有可能通过内部实现（**这是内窥镜无法实现的事情**，**更具体的什么手术需要两只手配合完成**） |
| 肾结石                                                       | 是                   | 是               | 是   | 内窥镜到达后夹出来就行了（所以要找一些自然腔道，而且需要一些操作的手术） |
| [percutaneous nephrolithotomy (PCNL) ](https://www.youtube.com/watch?v=-SVpt8T-0Yo) 应用于内窥镜解和超声解决决不了的大型结石 |                      |                  |      | 目前主流是使用微创将肾脏刺穿，如果能用                       |
| 胃造口术                                                     |                      |                  |      |                                                              |
| 经肛门全直肠系膜切除术 (trans-TME)                           |                      |                  |      | 手术流程太复杂了                                             |
| 胆囊切除术                                                   |                      |                  |      |                                                              |
| 阑尾切除术                                                   |                      |                  |      |                                                              |

内窥镜能够完成的手术：

* [Polypectomy](https://www.youtube.com/watch?v=v0fKD6BP9QI)

* [内镜黏膜切除术 (EMR)](https://www.youtube.com/watch?v=AI5zjDag1-w)
* [内镜黏膜下剥离术 (ESD)](https://www.youtube.com/watch?v=kngn2NY6gC8)

1. **Polypectomy**:
   - **Description**: Removal of polyps from the colon, stomach, or other parts of the gastrointestinal tract.
   - **Common Applications**: Colorectal polyps, gastric polyps.
2. **Endoscopic Mucosal Resection (EMR)**:
   - **Description**: Removal of larger superficial lesions or tumors from the gastrointestinal tract.
   - **Common Applications**: Early-stage cancer or large polyps in the esophagus, stomach, or colon.
3. **Endoscopic Submucosal Dissection (ESD)**:
   - **Description**: Advanced technique to remove deeper lesions or tumors from the gastrointestinal tract.
   - **Common Applications**: Early gastric cancer, esophageal cancer, large colorectal polyps.

___________

**现在的问题是，上面这些手术，内窥镜也能做，能不能找到符合NOTES但是内窥镜做起来很费劲的**

还是先多看几篇关于NOTES的论文或者科普吧

_______________________

更复杂一点的手术

* Peroral Endoscopic Myotomy (POEM) for Achalasia/经口内镜肌切开术 (POEM) 治疗贲门失弛缓症：
  * [临床实践](https://www.youtube.com/watch?v=NfGAkwXP-7A)
  * [原理介绍](https://www.youtube.com/watch?v=oSzdOLWj3Uw)

腹腔手术：阑尾切除术、胆囊切除术、胃空肠吻合术、结肠手术、脾切除术、腹部淋巴结切除术、子宫切除术、卵巢切除术、输卵管结扎术和抗反流手术。

最常见的是胆囊切除手术和阑尾切除术

自然孔腔内窥镜手术是指一种借由内窥镜通过人体的自然孔腔到达病灶位置的外科手术，（什么时候被提出），相较于开放的剖腹手术，NOTES存在诸多优点，可以避免切腹带来的伤口感染和切口疝的问题[]，实际上腹腔镜也可以很大程度上避免这个问题，腹腔镜端口尺寸已从12毫米（筋膜和皮肤缝合闭合）减小到5毫米（仅需要皮肤闭合），再减小到2·7毫米（根本不需要闭合）；但是相较于腹腔镜，NOTES仍有它独特的优势，对于与外界经自然腔道连通的器官，如胃，十二指肠，直肠，子宫等，NOTES可以在无创的条件下执行手术。

根据调研过往几十年NOTES相关临床报告，可以发现，NOTES主要分为两类，即Direct-target NOTES versus  distant-target NOTES

|                  direct-target                  |  distant-target  |
| :---------------------------------------------: | :--------------: |
| peroral endoscopic myotomy (经口内窥镜肌切开术) |  经胃阑尾切除术  |
|                                                 | 经阴道胆囊切除术 |
|                                                 |                  |
|                                                 |                  |
|                                                 |                  |
|                                                 |                  |

ESD不算是外科手术

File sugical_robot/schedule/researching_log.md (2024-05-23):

# 科研手册

来学校也已经3个月了，主要是在上课，但也花了一些时间在科研上，主要是看论文，零零碎碎的看了一些，主要是花在研究手部的震动上，但研究效果不佳，原因主要是这个研究比较冷门，而且目前很难用工程去解决这个问题；

想暂停一下这方面的研究，主要原因有以下几点：

* 临床上只在现象上描述了手部的生理震颤，并没有从根本解释震颤的原因（就算有，也无法使用工程的方法从根源上解决震颤
* 之前说要用装置检测生理震颤与手部信号之间的关系？
  * 首先我没有EMG这方面的基础
  * 其次生理震颤如此微弱的信号，在手指末端较为明显，小臂和大臂肌肉估计是很难捕获到
  * 这些都使得生理震颤肌肉信号的检测很难实现
* 而我们最初的工程目标，仅仅只是抑制手指末端震颤带来的影响。这个通过变阻尼-刚度控制方法应该可以实现，也即大幅度运动时采样小刚度-阻尼，而小幅运动，或者保持静止时大刚度-阻尼

综上所述，监测手部生理震颤信号不是唯一解，也不是最优解，还有其他方法用于判断操纵者手部控制状态：

* EMG检测手部肌肉

* 加速度计+IMU判断手部运动状态

这样的话，上周那篇论文也不是白看了，通过融合滤波实现手部运动状态的识别

3-25更新：

	为了发表ICARM会议论文，项目推进了不少内容，完成了主体的搭建和电机的初步调试；但是很多细节仍需要进行完善，下一个环节是整合我这边和亦达的部分，实线初步实验，然后在此基础上改进。为了能达到拿来用的水平，还需要完成很多工作：

* [x] finger gripper 的结构完善
* [ ] 养成强度校验的习惯
* [ ] 肘部夹持怎么优化
* [ ] 运算在哪里处理呢？我是说mapping的内容；如果在我的stm32上，那就最后传输的是从端的构型空间，无所谓了，大不了都传
* [ ] 主从之间如何通信
* [ ] 关于自己之前一直想做的

另外也要为自己考虑，可以把做出来的东西转化成专利：

3-27 ：初次提交论文后，开始完善手部grip的搭建

4-18更新：

	gripper部分搭建大致完成，准备装配出实物看看效果，可以的话真的想去写个专利，毕竟也做了一两个月；如果要写专利，那就需要做一些理论上的工作：

有一个很在意的事情，到现在我没有找到太多关于手术机器人把手的资料，因为这个比较小，而且它的**学名到底叫什么！！！**（达芬奇专利叫他 hand held part; 两篇论文都提到了pinch grip type和the power grip type.；gripper）

surgical robotic master console pinch grip

* [x] 研究人体手部解剖学，研究较好的把握姿态
* [ ] 查一下别的公司这方面的专利

## 手部运动状态检测装置设计

首先，要分析一下，这样一个装置是不是必要的，因为，就目前连杆的结构而言，不需要

之前研究了人体手部震颤相关的原理；了解了其大致种类，生理原理，诱发原因，主要特性等；但是由于神经解剖学过于复杂，很难做到在根源上消除抖动；

因此打算改变侧重点，主要先研究医生在手术时出现的抖动情况，再找一下普通人的相关数据——因为，我们希望我们的设备，能够保证医生在很累，或者实习医生手抖比较明显的情况下，克服这个抖动

* 当然，我一直觉得，增加关节的阻力是一个很好的消除抖动的方法；也不一定，

相关文章:

[临床医生震颤](https://academic.oup.com/icvts/article/23/3/410/1749883)

### 无刷电机选型

| -                                                            | 额定扭矩(Nm) | 堵转扭矩(Nm) | 尺寸(D,W_mm) | 质量(g) | 价格 |
| ------------------------------------------------------------ | ------------ | ------------ | ------------ | ------- | ---- |
| [HT3510](https://item.taobao.com/item.htm?id=541974032557&price=110-170&sourceType=item&sourceType=item&suid=c557422a-d396-4647-9955-912a780a9aa6&shareUniqueId=24219330256&ut_sk=1.ZCqn0g5LfBQDAJU0cqw9myYs_21646297_1699976702203.TaoPassword-QQ.1&un=32beb8314c8c26ae69e853a82a8667b3&share_crt_v=1&un_site=0&spm=a2159r.13376460.0.0&sp_abtk=gray_1_code_simpleAndroid2&tbSocialPopKey=shareItem&sp_tk=TjA3OFczNWNNbko%3D&cpp=1&shareurl=true&short_name=h.59mjHCS&bxsign=scdD4SNds2JY8LAejbRlaF2cHZ0bnrbuom0wnyfyPPWJK4xFZVTLp6WUyjpJYbiHopkgTLLe_-Hh8qQteMDhT0dFxRq8EYA6hByM6gpKMREWCN5KJ09TPur8SUddQtUhiTA&tk=N078W35cMnJ&app=chrome) | 0.13         | 0.16         | 40x25        | 73      | 170  |
| [HT4310]()                                                   | 0.25         | 0.37         | 49x24        | 113     | 240  |
| [HT4315](https://item.taobao.com/item.htm?spm=a1z10.5-c-s.w4002-18530239084.30.56cf71e73SiGRc&id=557446002311) | 0.65         | 0.8          | 49x31        | 158     | 240  |
| [HT5225](https://item.taobao.com/item.htm?spm=a1z10.5-c-s.w4002-18530239084.18.56cf71e73SiGRc&id=541701409289) | 0.45         | 1            | 59.6x43      | 330     | 305  |
| [HT6010]()                                                   | 0.8          | 0.9          | 68x30        | 247     | 260  |
| [HT100](https://item.taobao.com/item.htm?spm=a1z10.5-c-s.w4002-18530239084.32.56cf71e73SiGRc&id=558192875037) | 1.6          | 3            | 98.5x35      | 520     | 860  |
| [3](https://item.taobao.com/item.htm?spm=2013.1.w4004-18530239073.10.4c1717533HQrxr&id=569863396306) |              |              |              |         |      |
| [4](https://item.taobao.com/item.htm?id=602811939035&price=899&sourceType=item&sourceType=item&suid=25adeb1e-967a-4710-bebe-1503fe4e73e4&shareUniqueId=24228653984&ut_sk=1.ZCqn0g5LfBQDAJU0cqw9myYs_21646297_1700039516217.TaoPassword-QQ.1&un=32beb8314c8c26ae69e853a82a8667b3&share_crt_v=1&un_site=0&spm=a2159r.13376460.0.0&sp_abtk=gray_1_code_simpleAndroid2&tbSocialPopKey=shareItem&sp_tk=RWNLSlczaXJMRFA%3D&cpp=1&shareurl=true&short_name=h.5Q9giLj&bxsign=scdM22FPZ8IT_mBYKVgIG5eso-hq2ubDKey1OHX70MrL_es9O2LRGmy9_e-CMWbec5OnvPYLtsvgL4y2mhd-49RutaRMcJSHNwp89xtBNFJoti8fA9GYc--9GJaI6oEt7Fd&tk=EcKJW3irLDP&app=chrome) |              |              |              |         |      |

目前购买的是MF4015，额定扭矩是0.25NM，非常的高，最大扭矩能达到0.65，好像我不太需要这么大扭矩的电机，MF4005系列，扭矩小，体积也小，但是转速很快，似乎也不是我想要的，

以MF4015为参照物，我需要，扭矩更小的，还能实现FOC的电机3个；

同时问一下，ME系列都是不带驱动吗，我想买ME1605或者2605，但是似乎都是电驱一体的，就是要自己配驱动对吧。

目前来说，电驱一体力矩最小的只能选MF4005或者4010了，

还有另一条选择，选择ME+外带的驱动器，就是电机和驱动器分离的；这样会麻烦一点，但是可选的选项多一点

| -      | $\tau_0$ | $\tau_{max}$ | 精度 |
| ------ | -------- | ------------ | ---- |
| MF4015 | 0.25     | 0.65         |      |
| MF4005 | 0.07     | 0.25         |      |
| MF4010 | 0.15     | 0.33         |      |
| ME3506 | 0.06     | 0.09         | 14   |
| ME2605 | 0.04     | 0.06         | 14   |
| ME1605 | 0.01     | 0.01         | 14   |
|        |          |              |      |
|        |          |              |      |

### 结构转动惯量计算

| 转轴         | 转动惯量 |
| ------------ | -------- |
| pitch        | 2500     |
| yaw          | 7500     |
| 近端偏转关节 | -        |

## 变阻尼刚度结构

这个结构一定是要实现的，因为是消除抖动和实现力反馈的核心基础；

因此本周(11.9)可以先看一篇变刚度阻尼的文章，看看前人是如果实现这个功能的

在此基础上，学习、复现、改进功能

## 机械结构迭代

反思之前的结构，可以发现存在一些很明显的问题：

* 三连杆的结构，使得人体手指只能在一个弧面上运动，因此手指会比较别扭
* 5个串联关节直接运动不柔顺，原因如下：
  * 手臂和手腕分离控制，两者之间会相互影响
  * 微创手术的操纵端是可以全自由度自由运动的；而我们目前把

* 为什么要用电机而不是编码器
  * 首先，我认为，过于丝滑并不是一件好事情，它会出现一下两种不良结果：
    * 稳定性差，稍微有一些扰动，就会跳变
    * 无法实现定位，一松手就会垮掉
  * 其次，为什么要使用电机
    * 第一，达芬奇手术机器人的操纵端(console)就是使用的电机，而不仅仅是使用编码器，这个在这个[视频](https://www.youtube.com/watch?v=teRQr2qquJA)里面显示的很清楚了
    * 电机是升级版的编码器，它可以解决上面这些问题
    * 同时，通过算法设计，还可以实现更柔顺的控制
  * 关于一些质疑点：
    * 电机减速器妨碍人体运动：因为这是云台电机，额定扭矩够小，所以并没有出现明显的阻碍，这个可以通过数据来说明
    * 成本，电机成本大约是编码器的43-5倍

#### 一种贴合手肘的开关

设计目标：

* 可以放置手肘，让手肘很舒服
* 可以跟随手肘在平面上运动
* 能够调节位置

关于这个主体的设计，目前有几个想法：

1. 最简单就是一个球窝，与手肘贴合的地方使用较为柔软且摩擦系数较大的材料；
2. 在1的基础上，添加一个开合的结构，关于开合，可以用之前的弹簧结构？
3. 类似于柔性抓手？但是不知道抓力够不够

#### 肘部底座移动

根据陈老师的建议，底座可以变成平行四边形。对比一下它与正交导轨的优缺点

| -              | 优点                                           | 缺点                                                         |
| -------------- | ---------------------------------------------- | ------------------------------------------------------------ |
| 正交导轨       | 搭载效果比较好，可以搭载较大的平台             | 暂时不知道同时移动两个导轨效果如何，会不会卡住；需要配合额外的传动才能和电机转轴配合 |
| 平行四边形连杆 | 结构更简单；可以直接在转轴上配合电机或者编码器 | 怎么把手肘+三联杆放在这个四连杆上呢                          |

同时陈老师推荐

### 齿轮选型

md，齿轮这个东西，学了很多遍，参数什么的都记不住

最重要的三个参数：

模数：决定齿轮齿大小的参数

压力角：决定齿的形状

齿数：。。。

其它参数都可以根据这个算出来

* 中心距计算

  



安装距Hb=H0+D0/2 = 19

H0齿条节线高度（齿条总高度减去模数M）= 10-1 =9

D0齿轮分度圆直径（模数M乘以齿数Z）=  20

目前我要确定的是装配孔到转轴的距离 l1 = 19 - 3.9 =15.1

陈老师不推荐使用齿条：

* 悬臂梁，不稳定——解决方法，两端固定
* 没有进行比较好的封装：可能会卡到手什么的

推荐使用同步带，但是同步带有一个不太好的地方是，无法比较好的测量平动

### 配重设计

配重可以很大程度避免电机负载；之前用转动惯量算转矩的方法完全错误，重新使用sw估算了正反的转矩：

顺时针：

| -             | 总质量(g) | 质心距(mm) |
| ------------- | --------- | ---------- |
| 两个pitch杆子 | 102       | 83.5       |
| 两个杆子末端  | 10        | 176        |
| gripper       | 64        | 120        |
| 编码器        | 15        | 180        |

总：

目前配重的力矩偏大，有两种方法解决：

1. 减小力臂：重新打太贵了，84，不如重新买配重吧；改为臂长47
2. 减小配重：买不到130g的，

临时解决方案：

末端增加一个配重（20g）

### 装配

#### 滚动部分

获得所有零件以后，先将扭簧固定在圆柱体中；并用502加固，然后将电容压感传感器安装到两个手指夹上；再将手指及和压簧进行配合，并使用M2螺栓将其固定；

最后将圆柱体，与编码器进行固定（目前是编码器，后面不知道要不要换成电机）

#### 俯仰部分

关于pitch杆与编码器的连接——直接套上去就行，

pitch和yaw的连接也很简单，没问题

配重重新验算了一遍，没有啥问题，可能有一点的问题是，配重连接块和pitch杆连接的时候，**没有空间再上螺母，只能光凭螺纹固定**

#### 偏航部分

与电机连接，也是标准的连接；不过要先把电机固定到板子上

至此，RPY三个部分装配好了

#### 导轨装配

必然是要从下往上进行装配

先装第一层导轨，，然后将固定电机的部分装配到纵向板子上，将纵向板子固定到滑块上，

固定好齿条和电机到横向板子上

固定横向导轨，将横向板子固定到横向导轨

ok，差不多！

### hand grip

设计目标：即使传统的内窥镜把手上也有很多功能键按钮，为了实现手术机器人操控的高效性，需要至少在hand grip部分实现传统内窥镜的所有功能，通过左右手配合，实现1个人完成需要多人配合的任务

3.00mm

#### 拉簧选型

[跳转到弹簧选型](./manipulator_design/grip_part/grip_4_links_modle.md)

#### 按钮调试

1. 选择调试串口
2. 开通引脚，测试通过

#### pincher部分设计

首先要明确一个事情，我需要准确的摁压角度，还是只需要检测是否被摁压；为了

目前在这个上面遇到了比较大的阻碍，一时不知道该如何去设计，首先明确一些目标和任务吧：

* 要做到同步开合，因此角度肯定是要检测的
* 陈老师提出的，当夹持到组织以后

#### 无名指旋钮

这部分首先要完成的任务是，选择合适的电器元件，实现旋转的切换：

关于具体要实现哪些功能？

* **Suction**: remove fluids, debris, or tissue fragments to maintain a clear view.
* **Irrigation**: deliver fluids to cleanse the surgical area, remove blood, and improve visibility.
* **Drug Delivery**: deliver medications directly to specific areas within the body.
* **AIR insuffulator**: 
* **camera**



目前能够选择的电子器件包括：电位器、旋转按钮、微型编码器

| -          | 优点                             | 缺点                                                   | 尺寸(d x h)         |
| ---------- | -------------------------------- | ------------------------------------------------------ | ------------------- |
| 电位器     | 价格便宜，能通过程序灵活设置挡位 | 需要额外设计程序，将阻值设置为挡位                     | 22 x 18 + 6x22      |
| 旋转按钮   | 挡位分明                         | 需要较大的力气拨动旋钮，不够顺滑，且挡位越多电路越复杂 | 29 x 12 + 10 x 13.5 |
| 微型编码器 | 非常顺滑，精度高                 | 贵，有点大材小用                                       | 15x17               |

经过实验和测试，决定使用电位器；

接下来一步需要进行电位器调试和功能实现。电位器的调试可以直接使用正点原子代码，要实现功能，先编写代码逻辑：

ADC通道会读取一个值：adc_value：0-4096

如果我需要n个功能，那就是需要将4096个值分成n等分

使用case函数实现多个功能；也即输出多个结果

为了看一下别人是怎么设计的，这里专门去找了一下专利

* [专利一](https://pss-system.cponline.cnipa.gov.cn/documents/detail?prevPageTit=changgui)

* 受力分析

  具体的推导过程见 [四连杆力学模型](./manipulator_design/grip_part/grip_4_links_modle.md)

* 四连杆长度的确定，需要满足最大最远两个距离的限制

* 夹紧部分：夹紧部分的设计是为了在位控和力控之间切换；具体的结构和尺寸设计，见手记本
  * 夹紧部分的出发使用扳机+曲柄滑块实现；
  * 首先绘制出末端位置与theta之间的关系见文件【x_slide-theta】，为了满足连杆长度尽可能的小，将theta的活动范围锁定在x变化率最大的范围，同时满足最大值约束和行程约束，通过绘制出【x_slide-theta-slope.fig】确当theta范围为[pi/4, 5pi/12]（不对，这个范围永远会超过最大值限制，所以要先通过最大值确定theta的最小值）；求解出来L1 = 5.4；L2=9.8； theta_i = 37.7，对应行程x = 3
  * 
  * 

#### pinch_handle BOM

| -                | -    | 是否有发票 |
| ---------------- | ---- | ---------- |
| M2 x 30 双头螺杆 | >2   | 11         |
| M2 x 14 双头螺杆 | >1   | 11         |
| O8I4B3  轴承     | 4    | 11         |
| O5I2B2.5  轴承   | 4    | 11         |
| O3IiB1 轴承      | 4    | 11         |
| 大小齿轮         | 2    | 11         |
| 编码器           |      |            |
|                  |      |            |

**有限元分析**：

51假期回来以后学习了一下有限元，使用有限元分析了一下目前模型的结构强度

## 算法设计

这里是重点做文章的地方

无刷电机：BLDC

### 变刚度控制

搜索了无刷电机通过算法实现[弹簧阻尼]系统，有视频，但是没有讲怎么实现

突然想清楚一个事情，所谓变刚度，电机里面没有弹簧的和阻尼的，无论如果，你改变的只有输出的力，那就是，根据检测到的位置和和速度，结合你想要的K和D，就能计算出那个模型下对应的力矩，也就实现了所谓的变刚度，而现在FOC在底层已经给你实现了，那你需要改的只有电机输出的力矩，这不是很简单嘛！

[这是这个成熟的FOC旋钮项目](https://github.com/scottbez1/smartknob/?tab=readme-ov-file)

* 用电机实现弹簧阻尼模型

  
  $$
  F_{simu} = c \dot{q} + kq
  $$
  所以只用知道$\dot{q} + q$ 就能求出模拟的力，得到模拟的效果

  其中速度和位置都能通过编码测量出来，所以第一步，先看电机如何获取位置

### 变阻抗控制

### 如何判断state

现在是在搭一个简单的spring-damping 模型

## LOG

2024-1-5

 电机目前还在调试，感觉只差临门一脚了

如果能够实现目前这些功能：力矩，速度，位置

那我应该如何设计程序，实现我想要的功能呢

首先回答一下陈老师的问题：为什么不用编码器而是使用电机：

1-8 —— 1-9 都在修改机械结构

1-9：主要是注重齿轮和齿条的选择和设计

## 购买清单

[正齿轮](https://item.taobao.com/item.htm?id=40871095716&spm=a1z10.5-c-s.w4002-23781110036.13.73685ce9DFA1UE&skuId=4933148908846)

[齿条](https://item.taobao.com/item.htm?app=chrome&bxsign=scdxU6UZlD8STx8e0B3WOeNbG_oSU-mxxm6c8RZckjZ9J39XTlCU05NI5leP5mb9aOuXSJVe_P5BYj2HyYmSdQWn7Ws9PzyCn53TsVBLv9KUxpFqvej3YDS5BOIyga3U52e-NQ0ugacVtShJFxODJ11lw&cpp=1&id=40857110379&price=5.4-315&shareUniqueId=25046855230&share_crt_v=1&shareurl=true&short_name=h.5LKwapoE6ZBxnht&skuId=4936465785162&sourceType=item,item&sp_abtk=gray_1_code_simpleAndroid2&sp_tk=dktaZFdoS0dqQnA=&spm=a2159r.13376460.0.0&suid=1e254251-4eba-4384-88b0-6104b429fce9&tbSocialPopKey=shareItem&tk=vKZdWhKGjBp&un=e82a4c002eac03ff66b6cdab846c86ba&un_site=0&ut_sk=1.YrP3DXm%20P/8DAHTCsSqRTDiZ_21646297_1704769421744.TaoPassword-QQ.1)

[电机还要买](https://shop343206944.taobao.com/shop/view_shop.htm?shop_id=343206944)

[标准螺栓](https://detail.tmall.com/item.htm?app=chrome&bxsign=scdhHyCvblpQviJvM8zHlpSDlCNV7ZFsaTZeG89VEPWY1itVGhGe77yV9Lt_4502u3tMVQHC0KrHYo7y866ae69vCJJlWb5aSMXnM9oxHhlDI8Y3Hlro2NTxXdkT3BzOVHi3S5h6cMZPZhaB9Jnse_VXQ&cpp=1&id=587639753812&shareUniqueId=25051646208&share_crt_v=1&shareurl=true&short_name=h.5LsdUseJ8RPTc9P&skuId=4942035267147&sourceType=item,item&sp_abtk=gray_1_code_simpleAndroid2&sp_tk=T1ZuSFdoc1kwZU8=&spm=a2159r.13376460.0.0&suid=cb84e320-dcff-4180-b3e2-c89ec06c4df1&tbSocialPopKey=shareItem&tk=OVnHWhsY0eO&un=e82a4c002eac03ff66b6cdab846c86ba&un_site=0&ut_sk=1.YrP3DXm%20P/8DAHTCsSqRTDiZ_21646297_1704792246273.TaoPassword-QQ.1)、[平头螺栓](https://m.tb.cn/h.5K8AlHuOl5X6pWB?tk=HhR5WS1M5R5)

[螺母]()

[把手]()

[扭簧]()

## TO-DO-List

- [ ] 查一下怎么写专利——没做
- [ ] 设计一下肘部结构——然后找陈老师讨论一下——设计的不太行
- [ ] 查一下扭簧怎么装配——用不到了
- [ ] 研究一下“串联L三连杆”——开始打印，这个结构很好

2-19-2.29

- [ ] 调电机似乎不是当务之急——但是我喜欢搞这个，有空还是搞好
- [ ] 明确手术机器人的应用场景
- [ ] 打印好3连杆以后，改进前面部分结构

- [ ] 肘部结构仍不知道怎么去改进设计
- [ ] 改完先打印一个简单的试一试
- [ ] 

要干的事情其实很多，但是太多了又一下子不知道从何处做起，最后一个星期了，想想能做些什么吧；整体设计来说；手腕我暂时不知道怎么改才好

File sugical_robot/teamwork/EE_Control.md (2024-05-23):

# EE_Control

主端需要发送一系列信号到从端，包括：

* 五个角度
* 开合信号

关于五个角度，首先需要定义初始位置以及正负号（这个很好定义，基本上确定了，最好写一个文档规定好，方便团队之间看得懂）；一个初始位置（初始位置好定义，但是希望每次上电的时候能够自动回到初始位置）

* 如何让电机上电就达到设定的初始位置；首先电机肯定可以位置模式，电机的位置控制有两种模式，一种是绝对位置控制，（绝对位置还分四种，这里稍微记录一下，multi loop 角度可以超过360°，而且可以正反转；但是single loop只能在360°以内，且只能正转，不推荐；1和2的区别就是可以调速度，推荐2），另一种就是增量控制；可以先物理标记电机的零位，使得零位和

尝试使用CAN控制电机位置

有一个很严重的问题，位置控制模式的时候，不收敛，振动很大；通过减小速度可以减弱这个问题，但是无法从根本上解决（后续需要在代码内部再使用一次PD控制减弱这个震荡）

100 100

40 14

60 30

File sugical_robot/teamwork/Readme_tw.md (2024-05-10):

# Readme_tw

	这个文件夹主要用来记录团队写作记录，同时作为项目进度记录

	2024.5.9 暂定实现的目标是完成手术机器人实体的装配，同时能够完成一些简单的任务，如夹取物体。目前需要完成的主要工作：

* 主端目前还有两个关节没有调试完成（核心任务），需要完成的目标是，定义好五个关节角度正负，并实时的将五个角度信息传递到从端。
*

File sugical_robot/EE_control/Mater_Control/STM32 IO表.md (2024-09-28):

## 电机序号

| ID   | 位置       | 初始角度 |
| ---- | ---------- | -------- |
| 1    | 左；base左 | -60      |
| 2    | 左；base右 | -200     |
| 3    | 左；偏航   | -95      |
| 4    | 左；俯仰   | 10       |
| 5    | 右；base左 | 84       |
| 6    | 右；base右 | 147      |
| 7    | 右；偏航   | -188     |
| 8    | 右；俯仰   | 60       |

# STM32 IO表

编码器IO： PA0, PA1, PA4, PA5

..\..\Output\atk_f407.axf: Error: L6218E: Undefined symbol HAL_ADC_ConfigChannel (referred from adc.o).

| Channel | 位置          | 引脚               |
| ------- | ------------- | ------------------ |
| 0       | 左手滚动(PA0) | PA0                |
| 1       | 右手滚动      | PA2（因为1不好使） |
| 3       | 待定          |                    |
| 4       |               |                    |
| 4       | 左手夹取(PA4) | PA4                |
| 5       | 右手夹取      | PA5                |

预动作：

清除电机原有信息，上电

使用位置控制使各个关节回零到初始位置

读取电机状态；确定无误

使用手指摁捏表示操纵者准备开始操纵手术机器人

开始操纵：

电机切换到力矩模式，并保持力矩为零

两种传输模式：

根据设定的主端采样频率 f_m 采集角度信息，并向从端发送控制指令（两种模式）；

模式一：根据设定的发送频率$$f$$，向从端发送角度信息

模式二：增加”握手协议“，向从端发送命令，等待从端执行完毕后返回消息后再发送下一帧控制指令

为了避免主从不同步（操纵者的手比手术臂运动快）带来的信息丢失的问题，提出解决方案：

方案一：将命令缓存在一个数组中，
方案二：通过提供一个力反馈提醒操纵者？

用手捏pincher两次，作为开始控制的信号；当检测到gripper端编码器两次大幅度运动时（写检测和判断代码）

先实现DMA，然后写一下这个判断逻辑

* 成功实现DMA功能，现在将其移至到整体代码中-成功整合，遇到报错link 找不到函数的问题，因为没有添加对应=》成功整合代码；
* 

开始工作，进入while循环 

首先使用50Hz的频率采样读取电机角度，编码器角度

将读取的12个角度编码，通过CAN发送到从端单片机（这里写好了，但是需要整理）

```mermaid
graph TB
    A[开始] --> B[预动作]
    B --> C{电机状态}
    C -->|无误| D[使用手指摁捏]
    C -->|有误| E[错误处理]
    
    D --> F[开始操纵]
    F --> G[电机切换到力矩模式]
    G --> H[两种传输模式]
    
    H --> I[模式一]
    H --> J[模式二]
    
    I --> K[根据f_m采集角度信息]
    I --> L[向从端发送角度信息]
    
    J --> M[增加握手协议]
    J --> N[向从端发送命令]
    J --> O[等待从端返回消息]
    O --> P[发送下一帧控制指令]
```

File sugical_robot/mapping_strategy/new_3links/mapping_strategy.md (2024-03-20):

# mapping strategy

高效的映射策略可以带给surgeon更好的手术体验，从而提升手术安全性；主从式手术机器人的映射策略主要分为同构映射和异构映射；同构映射也即主从两端构型相同或者大致相似，对应的关节之间可以直接进行线性映射，而异构映射通常需要借助主从两端正逆运动学建立映射关系。虽然该结构在自由度布局时尽量保持了同构关系，但是由于主端为刚性连杆，而从端surgical arm由柔性的continuum构成，因此主端“three-link”和从端surgical arm为异构映射。This section mainly introduce the mapping strategy from master console to slave arm, 也即从端驱动空间[theta 1 ... theta 5] 到从端构型空间。（从端到底是构型空间还是驱动空间？）

常规的DH建模法对连续体模型并不适合，这里采用前人提出的“Constant Curve Modle”，该模型使用 ks 描述末端偏离轴心的偏转角度，使用phi描述由偏转引起的绕轴心的旋转。

A well-designed mapping approach can enhance a surgeon's overall experience and ultimately bolster surgical safety. In the context of master-slave surgical robotics, mapping strategies typically fall into two categories: isomorphic mapping and heterogeneous mapping. Isomorphic mapping involves directly translating the master-slave configuration when both ends share similar joints, while heterogeneous mapping often necessitates employing forward and inverse kinematics to establish a mapping relationship between master and slave ends. Despite efforts to maintain an isomorphic relationship in the layout of degrees of freedom, differences arise due to the rigid structure of the main end and the flexible continuum of the slave end surgical arm. Consequently, the mapping between the master's "three-link" structure and the slave's surgical arm structure differs. This section primarily focuses on elucidating the mapping strategy from the master console to the slave arm, specifically transitioning from the slave's drive space [theta 1 ... theta 5] to its configuration space.

前面两个关节符合同构关系，可直接建立线性映射关系如下：
$$
\Theta_1 , \Theta_2 = {} 
$$
对于后面3个异构关节，我们采用传统的笛卡尔空间增量控制方法，但是在求解过程中并没有借助中从两端的正逆运动学，而是通过两者之间的几何关系推导得到简洁的解析解，避免了复杂的计算。以下简单介绍推导过程：

isomorphism or isomerism

For the subsequent three heterogeneous joints, we employ the conventional Cartesian space incremental control method. However, during the solution process, we eschew dependence on the forward and inverse kinematics of both central ends. Instead, we derive a straightforward solution based on the geometric relationship between them. The following section provides a succinct overview of the derivation process:

DH部分删除的内容：

```
Figure 4 displays the integrated kinematic diagram of the master-slave system. For the rigid linkage structure in the master console, we adhere to the Denavit-Hartenberg (DH) convention, assigning coordinate systems to each joint. Applying the conventional DH method to the slave-end flexible continuum introduces significant computational complexity. Instead, we employ a constant curvature model, which is better suited for continuum modeling \cite{ref_22_jones2006kinematics}. Within this model, \(ks\) denotes the continuum's deflection angle from the axis, while \(\phi\) represents the rotational angle resulting from the superposition of two orthogonal deflections. For a proximal section, \(\phi\) is zero.

\begin{figure}[htbp] % 设置图片浮动位置
    \centering % 图片居中
    \includegraphics[width=0.5\textwidth]{ieeeconf/master-slave_DH.jpg} % 插入图片，替换 example-image 为你的图片文件名
    \caption{Integrated kinematic drawing of master  console(a) and slave manipulator(b),  Coordinates were set up and attached to each of the joints on the basis of the Denavit-Hatenberg (D-H) convention} % 图片标题
    \label{fig:example} % 图片标签，用于交叉引用
\end{figure}

For the distal sub-mapping task,
we need to keep the end poses of the three-link and proximal section the same. One approach ensures their rotation matrices R are identical. Directly solving for this condition algebraically is computationally intensive and may not always yield a solution. Thus, we adopt a geometric method to address this challenge, offering a practical solution without the drawbacks associated with algebraic resolution.
```

```
The ‘minimum angle theorem’ : When point \(A\) is projected onto plane \(BOC\), the projection line \(AB\) coincides with \(BO\) , and the projection of 
\(BC\) onto plane \(boc\) coincides with \(BO\), thus forming two angles,\(\angle ABC\) and \(\angle OBA\), \(\angle OBc\) respectively. The cosine of the angle between them can be expressed as: \(cos \angle ABC = cos \angle OBC \cdot cos \angle OBA\). 

\begin{figure}[htbp] % 设置图片浮动位置
    \centering % 图片居中
    \includegraphics[width=0.5\textwidth]{ieeeconf/minimun_angle.png} % 插入图片，替换 example-image 为你的图片文件名
    \caption{Explanation of 'minimum angle theorem'} % 图片标题
    \label{fig:example} % 图片标签，用于交叉引用
\end{figure}
```

偏转修改：

The main link's final x-axis corresponds to $x_{2}$, hence the angle with \(OC\) is $\theta_3$, corresponding to $\angle1$ in the diagram. The end effector's final x-axis corresponds to $x_{2}^{a}$, hence the angle with \(OB\)  is $ks$, corresponding to $\angle2$ in the diagram.
To solve for the angle $\Delta x$ between $x_{2}^{a}$ and $x_{1}$, it is also necessary to rely on projection relations and the law of cosines. By drawing auxiliary line \(OQ\) as the projection of \(OP\) on plane \(OBA\), three sets of equations can be obtained:

fig(b)中每个角度在fig(a)中都能找到对应的角度，POx_2 对应x0Ox2为thata3，记为角1；

角BOX2^a 对应x1^a O x2^a为\ks，记为角2

Specifically, angle \text{POx}_2POx2 corresponds to \text{x}_0 \text{Ox}_2x0Ox2 as \theta_3*θ*3, denoted as Angle 1. Angle \text{BOX}_2^aBOX2*a* corresponds to \text{x}_1^a \text{Ox}_2^ax1*a*Ox2*a* as \ks\ks, recorded as Angle 2.

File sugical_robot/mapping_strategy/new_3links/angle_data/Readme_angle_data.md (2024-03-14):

# Readme_angle_data

对于手部震颤实验；获取了5组震颤数据，并计算了平均值，通过画图将其可视化；

* [x] 获取了多组P数据，求平均值后将其绘制出来
* [x] 最好能够进行频域分析

对于卡尔曼滤波：

* 在matlab中实验KF后，对每组的data角度进行处理；

* [x] 得到5组KF处理后的KFdata
* [x] 求解对应的P_all_KF
* [x] 求平均值

绘制得到了KF处理后的P震动图像，结果好的有点出乎一辆

* 单个KF过滤图像
* 对比过滤图像

然后重复上述步骤，得到新的图像

对于支撑对比实现

绘制了两者对比的图像

## 论文需要的图

* [x] 多组位置平均的结果：avg_P
* [ ] 对avg_P 频域分析
* [x] KF处理后的结果，及其对比图
* [ ] 改善KF展示图
* [x] 有无支撑对比图

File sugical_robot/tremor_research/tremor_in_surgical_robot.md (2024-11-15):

# 手术机器人消抖

## 研究背景

what：什么是生理性震颤？

**生理性震颤**是正常人群中普遍存在的一种震颤类型，是身体部位快速来回运动的表现。

why：为什么会产生这个震颤？

医生怎么说？工程师怎么说？

* 临床定义：

  这种震颤由两种不同的振荡——**机械反射和中枢神经源性振荡**——叠加在不规则的肌肉力量波动和肢体位移的背景上。（但是具体是什么原因医生也没有搞明白）

  1. **机械反射振荡**：大多数正常受试者的主要频率成分。
     
     - 主要由身体的惯性和弹性属性决定，表现为阻尼振荡，响应于诸如肌肉单位放电不规则性和心脏收缩期血液喷射等脉冲扰动。
     - 机械反射的频率与关节的刚度（K）和惯性（I）相关，频率公式为 *w*=*K*/*I*。例如，肘部震颤的频率为 3-5 Hz，手腕震颤为 7-10 Hz，指关节震颤为 12-30 Hz。
     
  2. **中枢神经源性振荡**：(这里我其实还没有看懂)
     
     - 与运动单位活动的调节相关，这种振荡不仅仅是对感觉反馈的被动反应，而是主动驱动肢体振荡的节律性运动单位活动。
     - 中枢神经源性震颤的频率通常在 8-12 Hz 范围内，不受惯性或刚度的影响，也独立于拉伸反射的长度。这种振荡被认为源于中枢神经系统中的振荡神经网络。
     
  3. **反射机制**：
  
     - **振荡反馈**：由中枢神经系统的反射回路引起，当肌肉收缩或伸展时，肌肉梭的敏感性上升，会产生周期性反馈，增加肌肉活动的节律性。
     - **反射增益**：反射增益和传导时间的适当配合会导致反射激活振荡产生震颤。

如果没有人为的干涉，手术机器人在工作时末端会存在较为严重的震颤情况，这个是毋庸置疑，震颤主要来源于以下几个方面：

* 生理震颤是一种正常的、低频的肌肉微抖动，通常在成人中频率约为每秒10次。它是由多个突触耦合的神经系统与外部效应器的生物力学、物理和电特性之间的动态相互作用引起的。[PHYSIOLOGICAL TREMOR](https://scholar.google.com/scholar?hl=zh-CN&as_sdt=0%2C5&q=PHYSIOLOGICAL+TREMOR&btnG=) ，Tremor From Pathogenesis to Treatment。在长时间的劳作之后，生理震颤会加剧，疲劳引起的手部震颤 (FIT) 是一种不可避免的现象，它极大地限制了长时间腹腔镜手术的手术操作的准确性。肌肉疲劳引起的手部震颤具有高度非线性和非平稳特性，需要不同于传统滤波器的滤波策略。
* 关节编码器的数据有噪声，但是这个似乎非常的不明显这个看看用卡尔曼滤波能不能很好的解决。
* 呼吸带来的震颤虽然频率小，但是幅度远大于生理震颤，因此对呼吸的抖动进行抑制也是一个值得研究的内容
* 另外运动是不可能保持很直，尤其是在主从遥控的背景下（是否可以通过模式识别，识别出操作者的意图，进行一定的辅助）

但是这个噪声很小，只要设备够好，基本上不会出现很大的噪声：

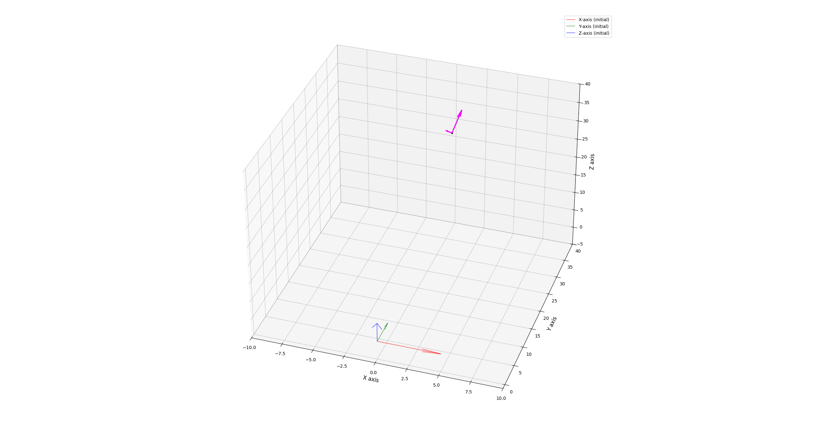
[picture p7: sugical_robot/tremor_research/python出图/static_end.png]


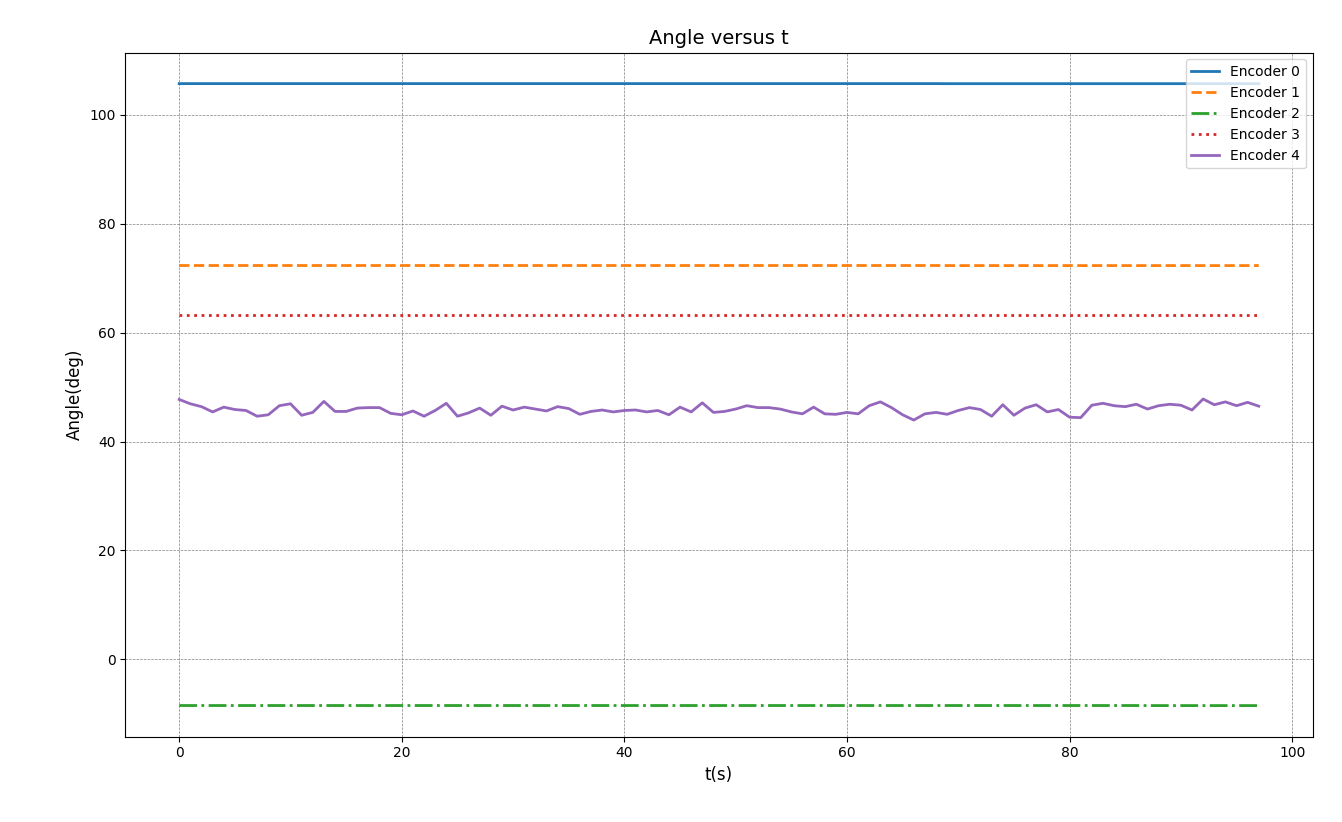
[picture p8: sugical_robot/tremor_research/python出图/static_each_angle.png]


但是，还是希望能够将这样一个震颤在3D条件下可视化出来。因此需要做一些工程上的事情：

1. 使用电脑接受CAN发来的数据，并存在txt文件中
2. python/matlab读取txt文件，然后根据之前的函数绘制末端点+箭头改变情况

### 大伙都说有，其实明显吗

[缝合模拟](https://www.youtube.com/watch?v=b09keuSVxwE)：在实验中没有观察到明显的震颤与手抖，因为在运动的过程中，生理震颤的影响几乎可以不略不计

[套环实验](https://www.youtube.com/watch?v=Oh-YZ2qMN3Q)：这个实验中也观察不到操作者手部明显的震颤

[直观的手部演示](https://www.youtube.com/watch?v=PBN54PNdr1U)：视频主要演示动态的过程，生理震颤带来的抖动在动态过程中

[套环视频](https://www.youtube.com/watch?v=pqrvG3chkdk)：也是动态的吧，几乎没有什么震颤

反思之前出现的问题，过于关注静态，而且是没有拖住的情况，但是实际手术中，手更多是一个运动的状态，这个时候，生理震颤反而不明显

尝试画一个circle，及时一些运动观察一下轨迹

### 消抖方法研究-别人是怎么做的：

* 低通滤波：手部是高频信号，而期望的输入信号是低频信号

  缺点：会使得信号存在延迟/低通滤波需要设置固定的频率阈值，导致了滤波结果损失了 部分信息，低通滤波仅能实现精度要求不高的震颤滤除

* 零相位滤波：无法应用于实时系统（不太懂零相位滤波的原理，只知道可以调相位）

* 傅里叶线性组合器：先对震颤信号进行建模，然后将震颤信号反向叠加到控制信号（有点像AirPods工作原理）

* 加权傅里叶线性组合器L可以估计任意近似周期的震颤信号——者手部生理震颤信号的频率、幅 值、相位进行估计建模，在此基础上生成一个频率和相位与震颤信号相同，幅 值与震颤信号相反的补偿信号来滤除震颤信号

* 卡尔曼滤波：利用惯 性测量单元测量手持显微外科仪器角速度，通过分析传感器噪声分量得到噪声 协方差

* 基于AR模型滤波：自适应滤波策略（这个看着就比较花哨比较难了）

* 自适应多步震颤预测策略：有效改进**传统滤波相位延迟问题**

* 基于EMD（多模态分解）的滤波方法

### 残余振动抑制

* ”机械臂关节摩擦引起的关节柔性对摩擦 进行建模“（逐渐抽象看不懂），**基于变结构控制设计的多状态反演控制方法** ；单关节摩擦建模（<font color = red>又为什么都是对摩擦进行建模呢</font>）
* 柔性环节简化，实现反馈线性化

## ！我怎么做

首先，我认为手术的人为误差并不只来源于生理震颤，除此之外呼吸引起的手指运动也是一个总要的影响因素，更重要的人手无法在空间中完成精准的运动，必然会出现偏差；前两者在静态误差中更为明显，后者主要影响动态误差，针对不同的情况，不同的震颤来源，需要采用不用的消除方法

此外，通过绘图发现，不同的【阻尼】对绘制的精度也有明显的影响；太小无法削弱生理震颤的影响，太大容易出现超调的现象；（陈老师似乎不喜欢搞阻尼控制？觉得会影响操纵者，希望是0阻尼情况下）

**震颤消除算法设计：**

首先，针对静态和动态需要一个识别器：

对静态的进行处理；一是通过看文章看一下能不能提出合适的算法

针对动态，需要识别出来是走直线还是曲线，另外需要讨论到底，二是提出一套针对于静和动的阻尼控制方法

### 针对constant震颤

采用类似于噪声抑制的算法（需要多了解了解）

一篇[TRO论文](https://ieeexplore.ieee.org/abstract/document/1391016)中采用[重复控制器](E:\GitHub\Mac_win\Mac_Win\sugical_robot\tremor_research\REF_TREMOR\Tremor_resolve\重复控制.md)的策略消除呼吸带来的影响

[具体方法看这里](E:\GitHub\Mac_win\Mac_Win\sugical_robot\tremor_research\REF_TREMOR\Tremor_resolve\Tremor_solve.md)

## 带限多重傅立叶

带限多重傅立叶，就是实用多个余弦函数对输入信号进行模拟，所谓带限即使设定一个组合余弦函数的的频率范围，并且讲频率均匀离散的分布到n，需要优化确定的参数就是每个频率函数对应的权重，可以得到一个输入模拟信号和输出合成信号的线性方程，文章使用了以下方法求解权重：

1. 最小均方根算法：一种滤波中常用的算法
2. 卡尔曼迭代算法，利用卡尔曼滤波的原理，构建权重相关的状态转移方程，即可使用卡尔曼算法进行迭代
3. 递推最小二乘算法(RLS)，原理和最小均方根基本相似，只是权重和递归增益的更新数学模型较为复杂
4. 

### 参数辨识

常见的方法有实验 辨识法和动力学建模计算法。 

作者认为：建模 精度限制，存在一定的误差。 

实验法：时域辨识和频域辨识

作者使用

### 作者的主从映射

因为不是直觉映射，所以映射关系绕了很多弯子，目标还是建立主端（输入端）的坐标变换和从端（输出端）之间的变换关系，之前我建立的映射关系就是：

* 位置缩放：提出一个根据主从端工作空间比例计算缩放比例的方法，比较科学
* 姿态相同

作者也是一样，不过作者一共转了4次，比较复杂

最小均方根（Least Mean Square，简称LMS）算法是一种自适应滤波器算法，用于调整滤波器的权重以最小化其输出与期望输出之间的均方误差。这个算法的主要应用领域包括信号处理、通信系统、自适应滤波、机器学习等。

以下是LMS算法的核心原理和步骤：

1. **基本原理**：LMS算法的核心思想是通过不断地调整滤波器的权重，使其输出逼近期望输出，从而最小化均方误差。这是一种迭代过程，通过不断观察实际输出和期望输出之间的误差来更新权重，以逐渐收敛到最优权重值。

2. **滤波器模型**：LMS算法通常使用一个线性滤波器模型。给定输入信号x(n)和滤波器权重向量w(n)，滤波器的输出y(n)计算如下：
  
   ```
   y(n) = w^T(n) * x(n)
   ```

   其中，w^T(n)表示权重向量的转置，* 表示向量内积。

3. **误差计算**：算法首先计算实际输出与期望输出之间的误差e(n)：
  
   ```
   e(n) = d(n) - y(n)
   ```

   其中，d(n)表示期望输出，y(n)表示实际输出。

4. **权重更新**：LMS算法的关键步骤是根据误差e(n)来更新滤波器的权重。更新的规则通常如下所示：

   ```
   w(n+1) = w(n) + μ * e(n) * x(n)
   ```

   其中，w(n+1)表示新的权重向量，w(n)表示旧的权重向量，μ（mu）是学习率，它决定了权重更新的步长。

5. **迭代过程**：LMS算法通过不断重复上述步骤，即计算误差、更新权重，来逐渐调整滤波器的权重，使输出逼近期望输出。这是一个自适应过程，通常需要多次迭代才能达到最佳权重值。

6. **收敛性**：LMS算法通常在某个误差阈值下或者在连续的迭代中停止。算法的性能和收敛速度与学习率μ的选择、滤波器的初始权重和输入信号的统计特性等因素有关。

LMS算法的一个重要应用是自适应滤波，用于去除信号中的噪声或调整系统参数以适应不断变化的环境。它也在机器学习中的在线学习和梯度下降算法中有广泛应用。通过逐渐优化权重，LMS算法能够有效地逼近最佳解决方案，从而在多种领域中发挥作用。

递推最小二乘算法（Recursive Least Squares，简称RLS）是一种自适应滤波器算法，用于估计滤波器的权重，以最小化均方误差。与LMS（Least Mean Square）算法不同，RLS算法具有递推性质，能够随着新的数据点的到来，连续地更新权重，而无需重新处理历史数据。这使得RLS在需要实时处理数据或在计算资源有限的环境中特别有用。

以下是RLS算法的核心原理和步骤：

1. **基本原理**：RLS算法的核心思想是通过递归地更新权重向量，以逼近实际输出和期望输出之间的均方误差最小化。算法随着新的数据点的到来，动态地更新权重向量。

2. **滤波器模型**：与LMS算法一样，RLS算法通常使用线性滤波器模型。给定输入信号x(n)和权重向量w(n)，滤波器的输出y(n)计算如下：
  
   ```
   y(n) = w^T(n) * x(n)
   ```

   其中，w^T(n)表示权重向量的转置，* 表示向量内积。

3. **误差计算**：与LMS类似，RLS算法首先计算实际输出与期望输出之间的误差e(n)：
  
   ```
   e(n) = d(n) - y(n)
   ```

   其中，d(n)表示期望输出，y(n)表示实际输出。

4. **权重更新**：RLS算法的关键是递归地更新权重向量。权重向量的更新规则如下：

   ```
   w(n+1) = w(n) + K(n) * e(n) * P(n) * x(n)
   ```

   其中，w(n+1)表示新的权重向量，w(n)表示旧的权重向量，K(n)是递归增益，P(n)是协方差矩阵的递归更新，它们都是关于历史数据的函数。

5. **递归增益更新**：递归增益K(n)的更新是RLS算法的关键。K(n)的更新规则通常如下：

   ```
   K(n) = P(n) * x(n) / (λ + x^T(n) * P(n) * x(n))
   ```

   其中，λ是一个小正数，用于避免除以零的情况。x(n)表示输入信号，P(n)表示协方差矩阵，它也是递归更新的。

6. **协方差矩阵的递归更新**：协方差矩阵P(n)也是递归更新的，通常使用以下规则：

   ```
   P(n+1) = 1/λ * [P(n) - P(n) * x(n) * x^T(n) * P(n) / (λ + x^T(n) * P(n) * x(n))]
   ```

   其中，λ是一个小正数。

RLS算法的主要优点是其快速收敛性和递归性质，使其适用于需要实时数据处理和动态权重更新的应用。然而，与LMS算法相比，RLS算法的计算复杂度较高，因此在计算资源有限的环境中可能不太适用。 RLSS算法在信号处理、自适应滤波、通信系统等领域有广泛应用。

## 开始实践

* 工具可以实时储存，这个太棒了

  存在.csv 文件中，通过pandas库获取到CAN数据帧，存储于<class 'pandas.core.series.Series'>数据结构中，不过有一些多余的信息需要删减

  并将每6帧数据存储到一个 6x8 的数组中

* 转码，将读取到的16进制CAN数据帧 转为可读的 十进制float数据

  成功转码，先将所有float都存到一个float[] decoded_floats 中，然后需要稍微处理一下，得到左手和右手的数据，每行都是5个

* 通过正向运动学，得到末端的信息e

  搞定了，见FK.py 文件

* 将这些信息全部存储下来绘制

  搞定，见 plot_traj.py文件

* 采集数据，需要设计几个动作，看看别人是什么做的

* 对比滤波的效果

### 数据采集

在论文[Empirical Mode Decomposition-based filtering for fatigue induced hand tremor in laparoscopic manipulation](https://www.sciencedirect.com/science/article/pii/S1746809416301264)中，作者设计了下面几个任务：

1. 在矢状面上进行动态线追踪：受试者 沿垂直平面上绘制的 25 厘米长线移动，这是腹腔镜常见的移动长度
2. 静态握持腹腔镜工具：要求所有受试者将工具握在给定点而不做任何移动

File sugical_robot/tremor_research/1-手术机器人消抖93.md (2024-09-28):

# 手术机器人消抖

[toc]

## 研究背景

手术机器人存在抖动：

* 手部生理颤抖（<font color = red>有论文支持？还没看</font>）

* 手术器械是柔性的，工作过程中存在震动

  刚性机械臂的振动抑制较为成熟，但是柔性机械臂需要对**结构材料分析，优化结构、改进材料**，需要进行参数辨识，常见方法包括：数学建模法、实验辨识法

### 消抖方法研究：

* [低通滤波](#subsectionA.1)：手部是高频信号，而期望的输入信号是低频信号

  缺点：会使得信号存在延迟/低通滤波需要设置固定的频率阈值，导致了滤波结果损失了 部分信息，低通滤波仅能实现精度要求不高的震颤滤除

* 零相位滤波：无法应用于实时系统（不太懂零相位滤波的原理，只知道可以调相位）

* 傅里叶线性组合器：先对震颤信号进行建模，然后将震颤信号反向叠加到控制信号（有点像AirPods工作原理）

* 加权傅里叶线性组合器L可以估计任意近似周期的震颤信号——者手部生理震颤信号的频率、幅 值、相位进行估计建模，在此基础上生成一个频率和相位与震颤信号相同，幅 值与震颤信号相反的补偿信号来滤除震颤信号

* 卡尔曼滤波：利用惯 性测量单元测量手持显微外科仪器角速度，通过分析传感器噪声分量得到噪声 协方差

* 基于AR模型滤波：自适应滤波策略（这个看着就比较花哨比较难了）

* 自适应多步震颤预测策略：有效改进**传统滤波相位延迟问题**

### 残余振动抑制

* ”机械臂关节摩擦引起的关节柔性对摩擦 进行建模“（逐渐抽象看不懂），**基于变结构控制设计的多状态反演控制方法** ；单关节摩擦建模（<font color = red>又为什么都是对摩擦进行建模呢</font>）
* 柔性环节简化，实现反馈线性化（**线性化这件事好像很重要，大概是可以用系统更加可控**）
* 主动控制抑振方法：**极点配置**来 改变系统阻尼，从而抑制机械臂振动
* 基于神经网罗的补偿原理震动控制，
* [输入整形](#subsectionA.zxsr)

## 前辈工作内容

主端消抖，提出了两种滤波算法：

* 最小二乘支持向量机卡尔曼滤波算法
* 用带限多重傅里叶线性组合器对震颤信号进行估计和滤除（**看不懂**）

从端振动抑制：

机械臂进行动力学分析和振动模态分析，得到机械臂的各阶振型和振动频率，通过实验和神经网络对振动参数进行辨识。然后设计一种输入整形器抑制振动

### 手部生理震颤分析

文中引用了一篇2017年”天津工业大学“的文章，其中使用imu和一个商用主动控制器测量了手部振动的信号，其频率主要为10Hz左右（之前更早的有人实验得出结论是手部不自在震颤为8-12Hz）

之前自己也做过类似的实验，但是没有考虑采样时间，也没有在频域上进行分析

但这一部分的结论就是：手部生理震颤的频率大于

### 最小二乘支持向量机卡尔曼滤波算法实现

卡尔曼滤波算法具有较好的预测性，不存在明显的延迟滞后，因此符合手术机器人所需要的实时性

作者使用[SVM](#SVM_intro)的原因是，默认情况下卡尔曼滤波的Q、R的均值为0，但是非线性系统不能简单的视为0（**所以这里为什么输入信号不是线性系统吗**），总之作者的目的是建立自适应的QR

训练集，通过训练集寻找需要调整参数QR与输入信号之间的数学关系

将非线性函数转化为线性函数（**不知道具体怎么转化的**）

构建SVM线性方程，同时作为约束条件

构建义 LS-SVM 优化问题

转化为对偶拉格朗日方程

KKT法对3个参数求偏导，构建线性方程，得到R和Q关于输入信号的回归模型

带限多重傅立叶，就是用多个余弦函数对输入信号进行模拟，所谓带限即使设定一个组合余弦函数的的频率范围，并且讲频率均匀离散的分布到n，需要优化确定的参数就是每个频率函数对应的权重，可以得到一个输入模拟信号和输出合成信号的线性方程，文章使用了以下方法求解权重：

1. [最小均方根算法](#LMS_intro)：一种滤波中常用的算法
2. 卡尔曼迭代算法，利用卡尔曼滤波的原理，构建权重相关的状态转移方程，即可使用卡尔曼算法进行迭代
3. 递推最小二乘算法(RLS)，原理和最小均方根基本相似，只是权重和递归增益的更新数学模型较为复杂
4. 

### 机械臂末端振动抑制

1. 建立机械臂末端动力学方程

2. 使用仿真软件分析振动频率

3. 借助振动抑制的方法消除从端抖动

   1. 零残余振动（ZV初始方法）
   2. 改善一点得到带限制条件的整形器（ZVD）
   3. 再宽限一点得到叫做EI的整形器？
   4. 为了解决延迟问题，引入负脉冲，得到SNA整形器

4. 提到了一个整形器鲁棒性的问题

   因为振动无法完全消除，所以需要设定一个阈值

### 参数辨识

常见的方法有实验 辨识法和动力学建模计算法。 

作者认为：建模 精度限制，存在一定的误差。 

实验法：时域辨识和频域辨识

作者使用

### 作者的主从映射

因为不是直觉映射，所以映射关系绕了很多弯子，目标还是建立主端（输入端）的坐标变换和从端（输出端）之间的变换关系，之前我建立的映射关系就是：

* 位置缩放：提出一个根据主从端工作空间比例计算缩放比例的方法，比较科学
* 姿态相同

作者也是一样，不过作者一共转了4次，比较复杂

## 一些意外收获？

* 除了盯着达芬奇手术机器人，还可多看看别的，其他赛道另辟蹊径
* 在验证主从控制结果的时候，可以把主从端的运动轨迹都画出来，这样不仅可以直观的看到控制结果，还能观测到滤波的结果

## Append

#### <a id="subsectionA.1"> 低通滤波 </a>

减弱高频部分并允许低频部分通过的方式来平滑或去除信号中的高频噪音、高频成分或快速变化的部分。

**特点和原理：**

1. **频率截止：** 低通滤波器通过设置一个截止频率（cutoff frequency）来决定哪些频率成分通过滤波器，而哪些被阻止。截止频率以下的信号成分通常会保留，而截止频率以上的信号成分则被削弱或抑制。
2. **频域表示：** 低通滤波可以在频域中表示为滤波器函数，描述了滤波器如何影响不同频率的信号成分。常见的低通滤波器包括巴特沃斯滤波器、Butterworth滤波器、椭圆滤波器等，它们在频域中有不同的响应特性。
3. **平滑信号：** 低通滤波器可以用于平滑信号，去除高频噪音或不必要的细节，从而产生更平稳和可读的信号。这在图像处理和音频处理中非常常见。

#### <a id="subsectionA.zxsr">整形输入</a>

[输入整形法]（Input Shaping）是一种振动抑制方法，通常用于控制机械系统或其他物理系统中的振动和摆动。这种方法的目标是通过对输入信号进行适当的形状调整，从而减少系统的振动或摆动。以下是关于输入整形法的一些基本信息：

1. **原理**：输入整形法的核心原理是通过改变输入信号的形状，以减小系统的共振频率或减少激励力的峰值，从而减少振动或摆动的幅度和影响。
2. **应用领域**：输入整形法通常应用于需要精确控制的系统，如机械臂、航天器、汽车悬挂系统、桥梁等。它有助于减小振动对系统性能和稳定性的不利影响。
3. **工作原理**：输入整形法通过设计适当的输入信号轮廓来实现。这些轮廓可以是一系列脉冲或阶跃信号，其时序和幅度经过精心选择以减小振动。这些信号的特点是能够减少系统在共振频率附近的振动。
4. **优点**：与传统的振动抑制方法相比，输入整形法具有以下优点：
   - 不需要额外的机械或电子设备，只需适当设计输入信号。
   - 能够在系统响应频率附近减小振动，有效地抑制振动。
5. **缺点**：输入整形法的设计可能相对复杂，需要对系统进行详细的建模和分析。此外，如果系统参数发生变化，可能需要重新设计输入信号轮廓。

总之，输入整形法是一种用于减小机械系统振动和摆动的有效方法，通过适当设计输入信号轮廓，可以在不引入额外硬件的情况下改善系统的性能。这种方法在需要高精度控制和振动抑制的工程应用中具有广泛的用途。



#### <a id= "SVM_intro">SVM</a>

#### <a id= "LMS_intro">LMS</a>

最小均方根（Least Mean Square，简称LMS）算法是一种自适应滤波器算法，用于调整滤波器的权重以最小化其输出与期望输出之间的均方误差。这个算法的主要应用领域包括信号处理、通信系统、自适应滤波、机器学习等。

以下是LMS算法的核心原理和步骤：

1. **基本原理**：LMS算法的核心思想是通过不断地调整滤波器的权重，使其输出逼近期望输出，从而最小化均方误差。这是一种迭代过程，通过不断观察实际输出和期望输出之间的误差来更新权重，以逐渐收敛到最优权重值。

2. **滤波器模型**：LMS算法通常使用一个线性滤波器模型。给定输入信号x(n)和滤波器权重向量w(n)，滤波器的输出y(n)计算如下：

   ```
   y(n) = w^T(n) * x(n)
   ```

   其中，w^T(n)表示权重向量的转置，* 表示向量内积。

3. **误差计算**：算法首先计算实际输出与期望输出之间的误差e(n)：

   ```
   e(n) = d(n) - y(n)
   ```

   其中，d(n)表示期望输出，y(n)表示实际输出。

4. **权重更新**：LMS算法的关键步骤是根据误差e(n)来更新滤波器的权重。更新的规则通常如下所示：

   ```
   w(n+1) = w(n) + μ * e(n) * x(n)
   ```

   其中，w(n+1)表示新的权重向量，w(n)表示旧的权重向量，μ（mu）是学习率，它决定了权重更新的步长。

5. **迭代过程**：LMS算法通过不断重复上述步骤，即计算误差、更新权重，来逐渐调整滤波器的权重，使输出逼近期望输出。这是一个自适应过程，通常需要多次迭代才能达到最佳权重值。

6. **收敛性**：LMS算法通常在某个误差阈值下或者在连续的迭代中停止。算法的性能和收敛速度与学习率μ的选择、滤波器的初始权重和输入信号的统计特性等因素有关。

LMS算法的一个重要应用是自适应滤波，用于去除信号中的噪声或调整系统参数以适应不断变化的环境。它也在机器学习中的在线学习和梯度下降算法中有广泛应用。通过逐渐优化权重，LMS算法能够有效地逼近最佳解决方案，从而在多种领域中发挥作用。

#### <a id= "RLS_intro">RLS</a>

递推最小二乘算法（Recursive Least Squares，简称RLS）是一种自适应滤波器算法，用于估计滤波器的权重，以最小化均方误差。与LMS（Least Mean Square）算法不同，RLS算法具有递推性质，能够随着新的数据点的到来，连续地更新权重，而无需重新处理历史数据。这使得RLS在需要实时处理数据或在计算资源有限的环境中特别有用。

以下是RLS算法的核心原理和步骤：

1. **基本原理**：RLS算法的核心思想是通过递归地更新权重向量，以逼近实际输出和期望输出之间的均方误差最小化。算法随着新的数据点的到来，动态地更新权重向量。

2. **滤波器模型**：与LMS算法一样，RLS算法通常使用线性滤波器模型。给定输入信号x(n)和权重向量w(n)，滤波器的输出y(n)计算如下：

   ```
   y(n) = w^T(n) * x(n)
   ```

   其中，w^T(n)表示权重向量的转置，* 表示向量内积。

3. **误差计算**：与LMS类似，RLS算法首先计算实际输出与期望输出之间的误差e(n)：

   ```
   e(n) = d(n) - y(n)
   ```

   其中，d(n)表示期望输出，y(n)表示实际输出。

4. **权重更新**：RLS算法的关键是递归地更新权重向量。权重向量的更新规则如下：

   ```
   w(n+1) = w(n) + K(n) * e(n) * P(n) * x(n)
   ```

   其中，w(n+1)表示新的权重向量，w(n)表示旧的权重向量，K(n)是递归增益，P(n)是协方差矩阵的递归更新，它们都是关于历史数据的函数。

5. **递归增益更新**：递归增益K(n)的更新是RLS算法的关键。K(n)的更新规则通常如下：

   ```
   K(n) = P(n) * x(n) / (λ + x^T(n) * P(n) * x(n))
   ```

   其中，λ是一个小正数，用于避免除以零的情况。x(n)表示输入信号，P(n)表示协方差矩阵，它也是递归更新的。

6. **协方差矩阵的递归更新**：协方差矩阵P(n)也是递归更新的，通常使用以下规则：

   ```
   P(n+1) = 1/λ * [P(n) - P(n) * x(n) * x^T(n) * P(n) / (λ + x^T(n) * P(n) * x(n))]
   ```

   其中，λ是一个小正数。

RLS算法的主要优点是其快速收敛性和递归性质，使其适用于需要实时数据处理和动态权重更新的应用。然而，与LMS算法相比，RLS算法的计算复杂度较高，因此在计算资源有限的环境中可能不太适用。 RLSS算法在信号处理、自适应滤波、通信系统等领域有广泛应用。

#### <a id= "shake_filter_intro">振动抑制</a>

常见的消除物理抖动的方法（**那为什么不用在主端消抖？？？**

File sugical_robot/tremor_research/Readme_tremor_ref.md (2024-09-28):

# Readme_tremor_ref

最早关于生理震颤相关的研究：

19世纪时候，Schafer和Horsley发现人体在运动过程中会出现10c/sec 的节律性震颤，最初认为这是由中枢神经，尤其是脊髓控制的无意识运动[1]。

1956年，John Marshall和E. Geoffrey Walsh为了进一步验证肌肉在有意识的运动过程中产生的节律性（震颤）现象的来源及机制，验证这种震颤是否与大脑皮层的信号有关，或者是由脊髓、神经元等更低级别的神经结构控制。他们首次将加速计佩戴在肢体不同部位（手腕、肘部、肩膀），然后进行一些自愿运动，如快速屈伸手腕，以记录过程中产生的震颤。记录了不同运动速度和负载条件下的运动的数据。

通过实验得到了以下结论：这种震颤频率通常在7到13次/秒之间，并且在不同的身体部位表现出相似的频率，说明这种震颤具有普遍性。（但是这个频率竟然是加速度，不是很能理解，为什么用加速度来描述震颤的频率）；震颤的幅度可能会随运动速度和负载变化，但频率相对恒定。**（显然这和之后人们的研究结果不同）**

儿童和成人在不同年龄段的震颤频率，发现震颤的频率随着年龄的增长而增加，这为他们假设震颤可能与神经系统的发育有关提供了支持。

震颤可能更多是由脊髓或更低层次的神经控制机制驱动，而不是由大脑中的α波节律直接引发的。

**正常的生理性震颤不是由运动神经元的同步放电引起的**。相反，震颤更可能是由多个运动单元的非同步活动引发的，而这些活动在机械加速度数据中表现为节律性震颤。虽然个别运动单元可以引发明显的机械效应，但震颤的复杂性超出了简单的同步放电解释。

**所以这个作者的主要贡献是进一步观察和验证了生理震颤的主要频率成分，同时确定震颤不是由简单的运动环路反射引起。**

一部分学者（Lippold、Redfearn和Vuco（1959））通过观察断开的四肢的传入神经可以消除8-12hz的震颤， 认为这种震颤和 肌肉反射弧有关；另一方面，1967年 Marsden 发现震颤独立于感觉反馈而产生，震颤峰并不仅仅是牵张反射机制运作固有延迟的结果"；同年Yap发现心脏活动是正常手指震颤的起源

1970年，LIPPOLD提出生理震颤（频率为8-12 Hz）与屈伸反射弧中的振荡有关；通过设计实验观察中指在一个脉冲下的振荡情况，发现会出现与生理震颤中8-12hz频率差不多的震颤，因此推测生理震颤和肌肉反射弧中的振荡有关，频率一致性支持了生理震颤的神经基础。作者还在肌电信号中观察到了与震颤同频的信号，表明生理震颤涉及神经机制而非单纯的机械共振；通过增加心跳频率观察到震颤频率不增加，震颤不由心脏作用引起，支持中枢神经源性振荡的观点。

1976年ENBLE 为了进一步确定观察到的8-12Hz生理震颤的神经机制，他在受试者的手指上放置200g左右的力传感器，并且记录负责手指伸展肌肉的肌电信号，通过数据处理，识别出8-12hz的信号，并比较震颤信号和EMG信号的相关性，进一步证明了生理震颤和肌肉运动单元的放电有关。

1996 年ENBLE和2001年GU ̈ NTHER DEUSCHL 总结了前人的工作，总结了各种常见震颤的机理，其中【生理学震颤】中总结了三种导致生理性震颤的原因：也即机械成分、神经中枢振荡引起的8-12Hz恒定频率的震颤、以及肌肉反射弧中不规则放电引起的震颤。

这些结论在后续需要避免手部生理震颤的论文中被反复引用，但是却没有更多学者投入到解剖学层面的研究，可能是因为它不是病理性疾病。

至此生理震颤的机理已经研究的差不多它是一种震颤在10Hz左右的肢体不自主震颤。
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

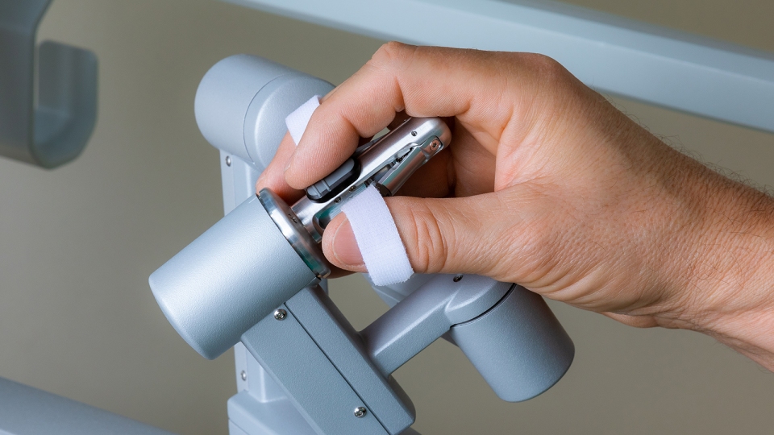
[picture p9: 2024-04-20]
sugical_robot/manipulator_design/images/endo-wrist-technologie.jpg

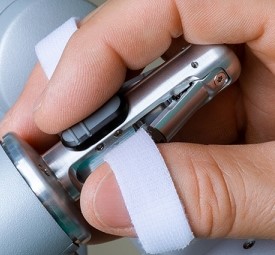
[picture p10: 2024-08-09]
sugical_robot/manipulator_design/images/pincher.jpg

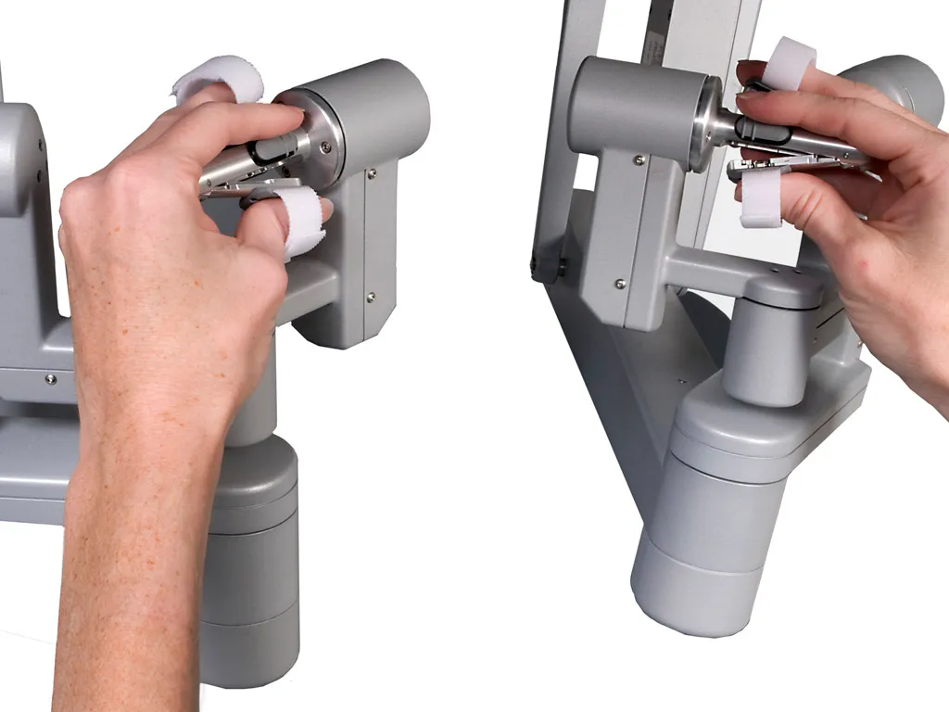
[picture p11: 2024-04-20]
sugical_robot/manipulator_design/images/master-grip-XI.webp

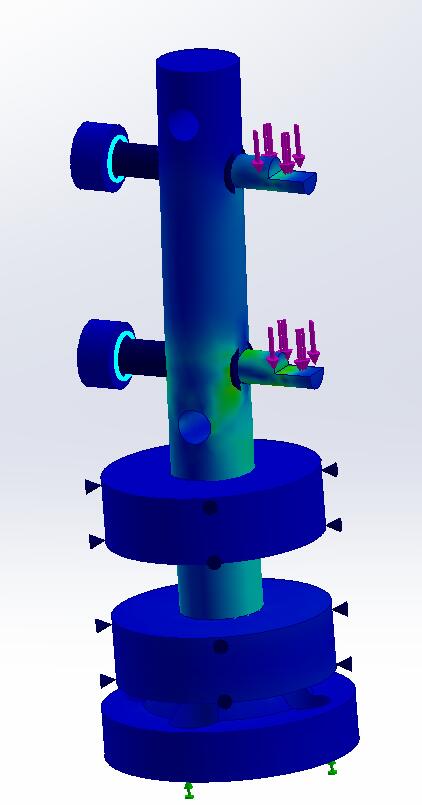
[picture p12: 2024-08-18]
sugical_robot/mechanical_model/树脂有限元仿真-应力.jpg

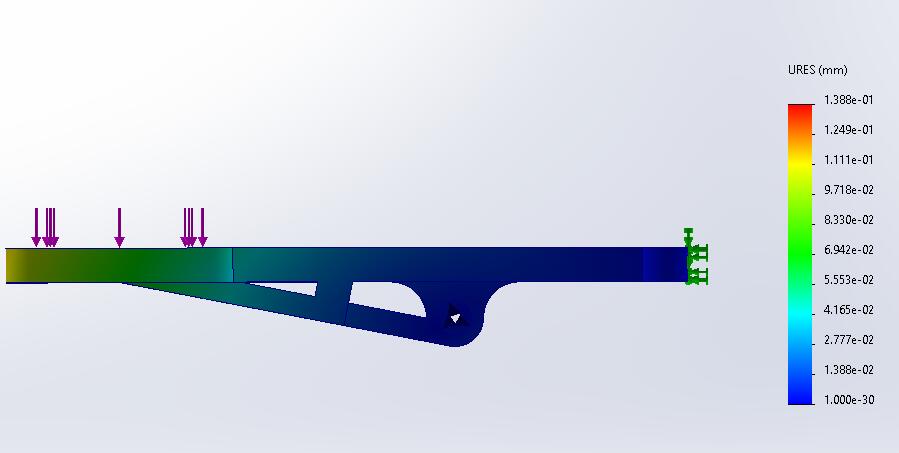
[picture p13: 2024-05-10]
sugical_robot/manipulator_design/grip_part/infinity_analyze/pinch_right_nilong_p.jpg

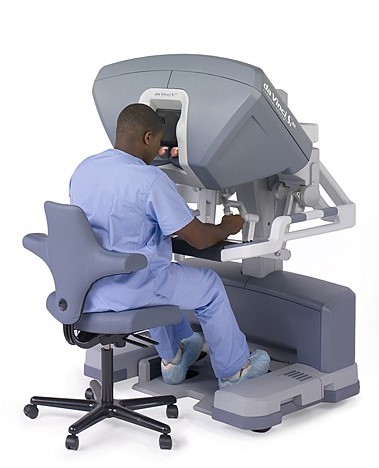
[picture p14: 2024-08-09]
sugical_robot/manipulator_design/davinci_master_console.jpg

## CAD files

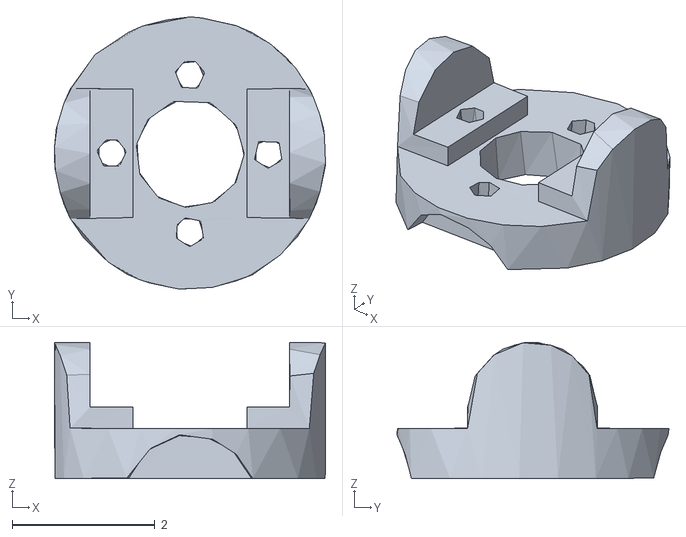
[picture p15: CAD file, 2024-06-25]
v1.3/binary/cylinderJointD1_c2.STL
3.80 x 3.82 x 1.91

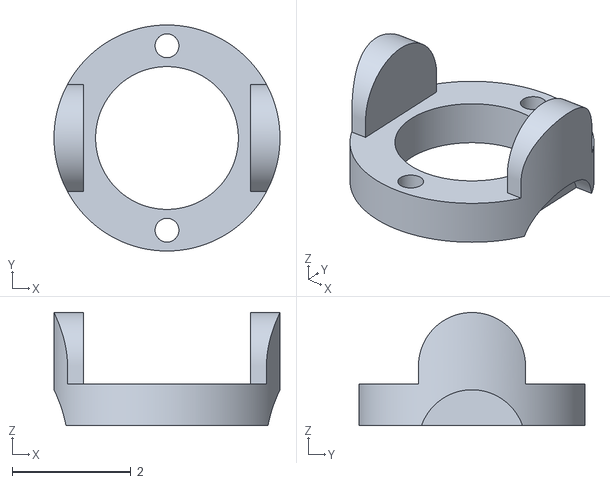
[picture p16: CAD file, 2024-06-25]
v1.3/binary/cylinderJointS1.STL
3.80 x 3.80 x 1.90

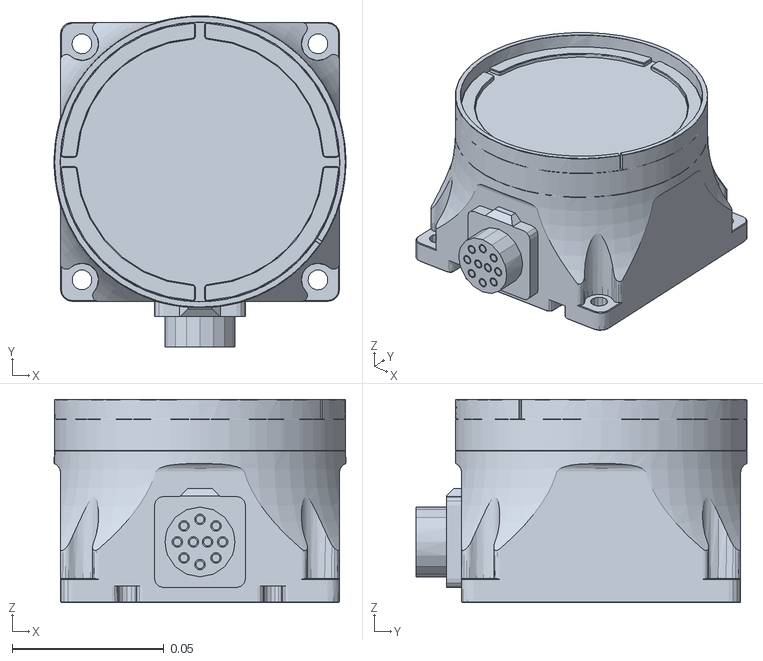
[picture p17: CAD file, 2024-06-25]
v1.3/binary/base_link.STL
0.0961 x 0.109 x 0.067

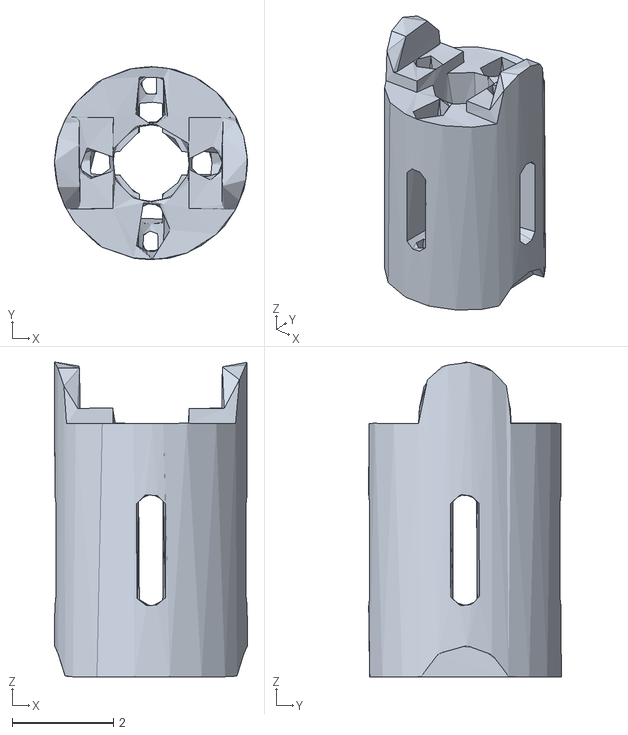
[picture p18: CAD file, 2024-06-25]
v1.3/binary/cylinderJointM1_c.STL
3.82 x 3.81 x 6.22

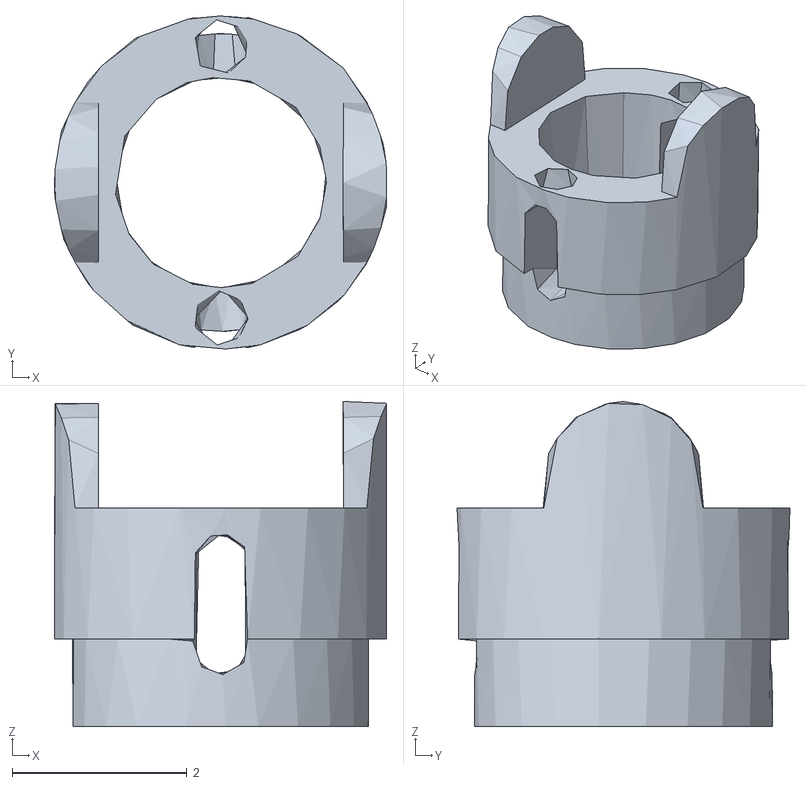
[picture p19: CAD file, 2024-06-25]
v1.3/binary/cylinderJointE1_c.STL
3.80 x 3.81 x 3.72

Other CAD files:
v1.3/binary/cylinderJointS1_c1.STL
v1.3/binary/cylinderJointD1_c.STL
v1.3/binary/cylinderJointD1.STL
v1.3/binary/cylinderJointM1_c1.STL
v1.3/binary/cylinderJointE1_c1.STL
v1.3/binary/cylinderJointD1_c1.STL
v1.3/binary/cylinderJointS1_c.STL
v1.3/binary/cylinderJointE1.STL

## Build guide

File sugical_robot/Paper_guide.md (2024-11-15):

# Paper_guide

注释：用于记录看过的每一篇论文

* [2015年NOTES手术机器人综述](https://link.springer.com/article/10.1007/s00464-014-3816-z)

  从自由度、**三角测量性**、分节几个方面总结了常见的手术机器人，特征上比较有参考性，但是文章太老了，不具有实时性

* [用于内镜柔性机器人的分析](https://ieeexplore.ieee.org/document/9779312?denied=)

  很全面的分析了柔性机器人在手术上的优缺点，以及具体挑战，可以启发类的论文，背景里面也可以做参考参考

* [介绍NOTES的综述](https://journals.lww.com/annalsofsurgery/pages/articleviewer.aspx?year=2008&issue=04000&article=00005&type=Fulltext)

  从剖腹开放手术开始，逐步介绍腹腔镜手术（MIS），NOTES（过程中有横向对比这几种手术的优缺点）

* [手术系统中用于驱动范围操纵的用户界面：范围界定审查](https://link.springer.com/article/10.1007/s00464-023-09981-0)

  终于有一篇类操纵端综述了，有点杂

* [直观的用户界面提高了内窥镜尖端控制的效率](https://link.springer.com/article/10.1007/s00464-014-3510-1)

  一篇老文章，说明直觉控制效率高于内窥镜

* [这篇文章虽然侧重MIS但是有一节介绍主从](https://ieeexplore.ieee.org/abstract/document/9779312)

  很好的总结了主从映射的问题

* [一个商用双通道手术机器人PDF](https://eaes.eu/wp-content/uploads/2016/11/FORGIONE_NOTES_and_TEM.pdf)

* [2015NOTES综述](https://academic.oup.com/bjs/article/102/2/e73/6141439#228305613)

  介绍了NOTES的历史，各个种类，以及存在的挑战

* [2023年-一种新型连续体外套管，具有改进的三角测量功能，适用于柔性机器人内窥镜检查](https://ieeexplore.ieee.org/abstract/document/10180212)

  阐述了一种远端设计可以实现改进的三角测量

* [纯介绍三角测量的](https://link.springer.com/article/10.1007/s00464-011-1650-0)

  也介绍了NOTES的优势

### surgical robot console

* [sigma7](https://ieeexplore.ieee.org/abstract/document/6094433)

### hand griper

[Olympus_design](https://www.olympus-global.com/technology/design/story/surgicalenergydevice/?page=technology_design) : 通过这篇官网链接，可以学习到世界顶级的手术器械的设计，从中获取灵感；比如如何强调直觉性、一些细节、如何改进

[endoscope_structure_introduction](https://www.youtube.com/watch?v=kHONXxQK3iE&t=504s): 油管一个十分详细介绍内窥镜各个结构的视频

[How endoscope work](https://clinicalgate.com/how-endoscopes-work/)

跟多文章见文件夹[manipulator design/readme]

## tremor

* [上古介绍肌肉疲劳震颤的文章](https://www.sciencedirect.com/science/article/pii/S0363502379801276)

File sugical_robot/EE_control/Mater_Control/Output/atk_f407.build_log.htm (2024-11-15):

µVision Build Log

Tool Versions:

IDE-Version: ¦ÌVision V5.14.0.0
Copyright (C) 2015 ARM Ltd and ARM Germany GmbH. All rights reserved.
License Information: ouch Administrator, 1, LIC=ATTQ1-C51MJ-NNIAF-615JW-7AGNI-9GD5I
 
Tool Versions:
Toolchain:       MDK-ARM Standard  Version: 5.14.0.0
Toolchain Path:  D:\Keil_v5\ARM\ARMCC\Bin
C Compiler:      Armcc.exe V5.05 update 1 (build 106)
Assembler:       Armasm.exe V5.05 update 1 (build 106)
Linker/Locator:  ArmLink.exe V5.05 update 1 (build 106)
Library Manager: ArmAr.exe V5.05 update 1 (build 106)
Hex Converter:   FromElf.exe V5.05 update 1 (build 106)
CPU DLL:         SARMCM3.DLL V5.14.0.0
Dialog DLL:      DCM.DLL V1.13.1.0
Target DLL:      STLink\ST-LINKIII-KEIL_SWO.dll V2.0.14.0_KEIL
Dialog DLL:      TCM.DLL V1.14.4.0

Project:

E:\GitHub\Mac_win\Mac_Win\sugical_robot\EE_control\Mater_Control\Projects\MDK-ARM\atk_f407.uvprojx
Project File Date:  08/06/2024

Output:

Build target 'CAN'
compiling DataTransmission.c...
linking...
Program Size: Code=19468 RO-data=13772 RW-data=480 ZI-data=2856  
FromELF: creating hex file...
"..\..\Output\atk_f407.axf" - 0 Error(s), 0 Warning(s).

Collection of Component include folders:

  E:\GitHub\Mac_win\Mac_Win\sugical_robot\EE_control\Mater_Control\Projects\MDK-ARM\RTE
  D:\Keil_v5\ARM\PACK\Keil\STM32F4xx_DFP\2.15.0

Collection of Component Files used:

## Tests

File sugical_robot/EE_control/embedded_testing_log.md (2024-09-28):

# embedded_testing_log

  ```
  目前可以接收数据帧，但是，不知道电机的数据帧在哪里;
  看样子，我自己也没搞明白，can是怎么进行接收数据的
  下午具体看看can是怎么接收的吧，先把接收原理搞明白
  
  1-18 8点
  尝试替换学长的can.c文件
  先将之前的进行备份
  
  失败，连信号都没有
  成功——是之前底层参数没有设置好的原因
  9点，成功将学长can代码融合，替换掉正点原子自带代码，解决了bug，但是不知道具体原因是什么
  
  但是目前还是没有实现接收
  试一下用can分析仪发送能不能实现——成功接收分析仪发来的消息；因为之前是loop模式
  但是学长的代码无法实现接收——因为开启了CAN1中断？
  
  ```

  ```
  逐一排查哪个函数的问题：
  初始化：对了一遍，大概没问题吧
  HAL_CAN_MspInit() ： 没有问题
  滤波器——有重大嫌疑
  实锤了，滤波器里面的id；是他妈的141
  
  __ NIV ___
  同样的，不知道为什么开了中断就接收不到了
  试一下不开中断，电机能不能正常收指令，如果可以，那中断就不开——测试，没有中断电机正常工作
  
  ___ Filter___
  现在搞明白啦，你那个标识符不对的话，根本是识别不到你发过来的信号的；
  比如
  ```

```
1. 确定一下电机是绝对编码还是增量编码（也即上电为0还是0位永远不变）——真牛逼两个都行
2. 确定一下正反返回的速度是不是一样的——逆时针为正

```

4-24 :尝试将我这边读取的数据存储在一个数组里面后通过CAN发送到亦达的单片机

首先数据都可以直接存在CAN_sending_para这个1维数组中

```c
				CAN_sending_para[3] = motor_pitch_para[2];
				for (int i = 0; i < 5; i++) {
						printf("%f ", CAN_sending_para[i]);
				}
				printf("\n"); // 换行
```

也成功通过send_CAN_array(motorId_yaw);函数向目标地址发送了信息

接下来尝试在F1上实现CAN通讯，但是目前的问题是HAL_CAN_AddTxMessage(&hcan, &g_canx_txheader, msg, &TxMailbox) != HAL_OK

目前的问题是，单挑数据发送可以收到，但是数据多了，是不是有冲突的问题？

看一下同时发5个，是接收5个还是一个  = 》不是1也不是5，是4？？？

**尝试在发的时候加一个delay，可能发的太快了，接收方来不及接收**

既然不能在一个循环中收完，那我就尝试循环5次接收完(没用)

* 尝试在一帧中发5个double：不可能实现，因为一个double就占了8个字节；后面可以换成更小的数据类型
* 尝试打开中断：打开中断以后，连正常的接收都接收不了了（玩锤子；=》中断可以！
* 把double换成了float（不是重点），成功实现了数据的转码=》发送=》解码（存在一个问题就是id和数据偏移）

使用正点原子的历程成功实现了发送，再试一下接收

```C
		send_CAN_array(1);
		for ( i = 0; i < 8; i++)
            {
                canbuf[i] = cnt + i; /* 填充发送缓冲区 */
						}
            res = can_send_msg(0X12, canbuf, 8); /* ID = 0X12, 发送8个字节 */

            if (res)
            {
                printf("send failed. \r\n");
            }
            else
            {
                printf("already send \r\n");
            }
            								
		rxlen = can_receive_msg(0X141, canbuf); /* CAN ID = 0X12, 接收数据查询 */

        if (rxlen) /* 接收到有数据 */
        {

            printf("\r\n already receive the msg \r\n");
            for (i = 0; i < rxlen; i++)
            {
								usart_show_xnum(canbuf[i], rxlen);
            }
        }
```

ok！发送和接收都能成功实现，接下来尝试一下连接两块单片机

成功对接单片机；接下来就是将数据整理好发去（实际上已经整理好了，不过是一组发5个

4-28：

现在存在的问题是，ID和数组存在错位的问题

* 尝试一：发送单条数据，看会不会错位：单条数据不错位。。。

```
//	uint16_t TH = 65535; //反转阈值用来将获取到的参数修正为负数
//  uint16_t iq;		//力矩电流
//  uint16_t speed; //速度
//	int32_t Speed;
//	uint16_t state[3]; 

//		iq =(uint16_t)(((uint8_t)rxbuf[3]<<8)
//									|((uint8_t)rxbuf[2]<<0));
//		if(iq > 60000) {
//			IQ = -(TH-iq);
//			printf("{motorTnfo}%d",IQ);
//			printf(",");
//		}else{
//			IQ = iq;
//			printf("{motorTnfo}%d",iq);
//			printf(",");
//		}

//	//	printf("%d",iq);
//	//	printf(",");
//		
//		speed =(uint16_t)(((uint8_t)rxbuf[5]<<8)
//										 |((uint8_t)rxbuf[4]<<0));
//		if(speed > 60000) {
//			Speed = -(TH-speed);
//			printf("%d",Speed);
//			printf("\n");
//		}else{
//			printf("%d",speed);
//			printf("\n");
//		}
```

## 6-3：购买完电机

* 首先给所有的标ID：

  | ID   | 位置       | 初始角度         |
  | ---- | ---------- | ---------------- |
  | 1    | 左；base左 | 108 // 0         |
  | 2    | 左；base右 | 168 => 93 =>-113 |
  | 3    | 左；偏航   | -95              |
  | 4    | 左；俯仰   | 10               |
  | 5    | 右；base左 | 100 =>-25        |
  | 6    | 右；base右 | 130 => 77        |
  | 7    | 右；偏航   | 180              |
  | 8    | 右；俯仰   | 60               |

  为了测试Id是否成功设置，使用如下代码检查：

  可以给一个很小的力矩值，也可以开\关交替（选择后者）

  ```c#
  		while(1)
  		{
  			
  			for(int test_id = 0; test_id < 8; test_id++)
  			{
  				motor_stop(motor_IDs[test_id]);
  				HAL_Delay(3000); // 观察现象
  			}
  //			if (motor_state == 1)
  //			{
  //				motor_close(motor_IDs[test_id]);
  //					motor_state = 0;
  //					HAL_Delay(3000); // 观察现象
  //			}
  //			else if(motor_state == 0) {
  //				motor_start(motor_IDs[test_id]);
  //				motor_state = 1;
  //				HAL_Delay(3000);
  //			}
  		}			
  ```
  
  成功设置了ID，并验证了8个通道的可行性；中间遇到了一个问题，就是连接在总线上数目超过两个时就会出现接收不到信号的问题，后面了解到只需要打开起始端和终点端的电阻即可。
  
* 接下来试一下读取8个电机的角度；

  * 不能使用start函数，会卡死，毒瘤函数，所以就不要先断电然后上电的步骤了

  * 初始位置终于搞定了，对于纵向的电机，需要注意，由于初始多圈角度是取决于单圈角度，满足

    theta_mul = theta_sig , theta_sig < 180

    theta_mul = theta_sig - 360, theta_sig >180

    因此，要养成用完以后拉回最后面的习惯

## 6-6 将角度发到上位机

目前我有一个长度为12的float的数组，我要将其用 2 x 12个bytes 的数据表示：

对于每个数，首先我需要将其转化为整数（四舍五入），然后使用两个字节存储这个整数，为了区分正负号，使用最高位作为标识符

12个角度对应的范围：

| id   | range   |
| ---- | ------- |
| 1    | [0,500] |
| 2    | [-]     |
| 3    |         |
| 4    |         |
| 5    |         |
| 6    |         |
| 7    |         |
| 8    |         |
| 9    |         |
| 10   |         |
| 11   |         |
| 12   |         |

## 7-30迭代了结构以后新调试

* [x] 首先在串口读取每个角度信息

  电机8读不到数据，每一次读到都是0，但是只读单个电机的时候角度是正常的；解决：在发送索要角度数据时加一个2ms的延迟，使得有足够时间处理中断内容

* [ ] 编写mapping.c 文件完成matlab中映射实现（**大工程**）

  * [ ] 驱动空间到主端关节空间映射

    已经有的参数是 十个角度信息，分为两组，每组
    
    * [x] 编写调试[plannar_5_bar_fk] 函数
    
      ```c
      			Plannar5BarFKResult fkResult = plannar_5_bar_fk(motor_angles[0], motor_angles[1]);
      			for (int i = 0; i < 5; ++i) {
          printf("Forward Kinematics Result: x = %f, y = %f, u3 = %f\n",
             fkResult.xc, fkResult.yc, fkResult.u4);
      			}
      ```
    
    * [x] 编写、调试驱动空间到关节空间函数
    
      ```c
      			// test mapping_master_drive_joints 
      			mapping_master_drive_joints(motor_angles);
      			int i;
      			for(i = 0; i < 10; i++) {
          printf("array[%d] = %f ", i, joint_angles[i]);
      }
      			printf("\n");
      ```
    
    * [x] 从主端 关节空间到从端关节空间
    
    * [ ] 严谨一点的话，生成100组数据，对比matlab和c运行的结果

## 8.6 完成大体代码的整理与融合

* bug1：映射计算的过程没有注重角度制和弧度制

* D1的变换是反的，其它几个参数，初始值不为零=》

  * [x] 先把计算出来的主端参数验证一下，

    ```c
    	if(offset==0)
    	{
    		printf("theta1: %f, d2: %f, theta3: %f, theta4: %f, theta5: %f \r\n", radians_to_degrees(joint_angles[0]), joint_angles[1], 
    		radians_to_degrees(joint_angles[2]),radians_to_degrees(joint_angles[3]), radians_to_degrees(joint_angles[4]));
    	}
    			if(offset==0)
    	{
    		printf("D1: %f, alpha2: %f, Phi3: %f, alpha4: %f, Theta5: %f \r\n", slave_joint_angles[0], radians_to_degrees(slave_joint_angles[1]), 
    		radians_to_degrees(slave_joint_angles[2]),radians_to_degrees(slave_joint_angles[3]), radians_to_degrees(slave_joint_angles[4]));
    	}
    ```
  
  * [x] 然后从端的关节参数：其中\Phi3的验证比较困难，通过采取STM32串口打印的数据，和matlab进行比较，没有问题
  
  * [x] 最后一步到单元关节的参数

## 模式控制切换

goal：通过按key_up键实现模式切换，红色灯对应绝对模式，绿色对应增量模式

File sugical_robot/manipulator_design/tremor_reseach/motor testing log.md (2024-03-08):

# motor testing log

### 2024_3_2

* 将读取的数据传入到motor_para数组中

  ```c
  			cnt++;
  			test_param_tran(cnt, motor_para);
  			printf("State array: [t: %u, tau: %u, v: %u, P; %u]\n", 
             motor_para[0], motor_para[1], motor_para[2], motor_para[3]);
  ```

  通过验证，该函数可以将motor_ctrl中读取电机状态的函数传递到main函数中

  目前已经可以读取电机数据了

* 使用很小的力矩，读取编码器的数据P，并找到P和角度之间的关系

  读取的四个数据，前三个都没有问题，感觉位置有很大问题

  1622550009861 State array in motor_ctrl: [t: 25, tau: 5, v: 0, P; 98]

  1622570002462 State array in motor_ctrl: [t: 25, tau: 7, v: 0, P; 24]

  162251004019862State array in motor_ctrl: [t: 25, tau: 10, v: 4, P; 198]

  编码器虽然精度不太行，但是至少逻辑没问题

  因此**解码的函数**有很大问题

* 

### tmp_code

```
//				printf("\r\n read to use USART to test CAN \r\n");
//			HAL_CAN_RxFifo0MsgPendingCallback(&g_canx_handler);
//			uint8_t rx_data_length = can_receive_msg(1, rx_buffer); /* recieve 88 00 00  */
////					
//					if (rx_data_length != 0)
//					{
//						printf("\r\n already receive the msg \r\n");
//						for (i = 0; i < rx_data_length; i++)
//            {
//								usart_show_xnum(rx_buffer[i], rx_data_length);
//            }
////						uint8_t command_byte = rx_buffer[0];
////						if (command_byte == 0xA1)
////            {
////                uint8_t temperature = rx_buffer[1];
////                int16_t iq = rx_buffer[2] + (rx_buffer[3] << 8) ;
////                int16_t speed = rx_buffer[4] + (rx_buffer[5] << 8);
////                uint16_t encoder = rx_buffer[6] + (rx_buffer[7] << 8);
////								 printf("Temperature: %d C, IQ: %d, Speed: %d dps, Encoder: %u\n",
////                       temperature, iq, speed, encoder);
////								
////                // ????? motor_temperature, motor_iq, motor_speed, encoder_position ????????
////            }
//					}
			
//        key = key_scan(0);

//        if (key == KEY0_PRES)           /* KEY0°´ÏÂ,·¢ËÍÒ»´ÎÊý¾Ý */
//        {
//						printf("\r\n torque1 \r\n");
//						
//					
//            start_res = can_send_msg(motorId, torque_control, 8);    /* ID = 0x12, ·¢ËÍ8¸ö×Ö½Ú */
//					
//					// recieve the data from motor 
//						uint8_t rx_data_length = can_receive_msg(motorId, rx_buffer); /* recieve 88 00 00  */
//					
//					if (rx_data_length != 0)
//					{
//						uint8_t command_byte = rx_buffer[0];
//						if (command_byte == 0xA1)
//            {
//                uint8_t temperature = rx_buffer[1];
//                int16_t iq = rx_buffer[2] + (rx_buffer[3] << 8) ;
//                int16_t speed = rx_buffer[4] + (rx_buffer[5] << 8);
//                uint16_t encoder = rx_buffer[6] + (rx_buffer[7] << 8);
//								 printf("Temperature: %d C, IQ: %d, Speed: %d dps, Encoder: %u\n",
//                       temperature, iq, speed, encoder);
//								
//                // ????? motor_temperature, motor_iq, motor_speed, encoder_position ????????
//            }
//					}
//            if (start_res)
//            {
////                lcd_show_string(30 + 80, 170, 200, 16, 16, "Failed", BLUE); /* ÌáÊ¾·¢ËÍÊ§°Ü */
//							 usart_show_string("Faild");
//							
//            }
//            else
//            {
////                lcd_show_string(30 + 80, 170, 200, 16, 16, "OK    ", BLUE); /* ÌáÊ¾·¢ËÍ³É¹¦ */
//							usart_show_string("OK");
//            }
//        }
//        else if (key == WKUP_PRES)      /* WK_UP°´ÏÂ, ¸Ä±äCANµÄ¹¤×÷Ä£Ê½ */
//        {
//            mode = 0;
//            /* CAN³õÊ¼»¯, ÆÕÍ¨(0)/»Ø»·(1)Ä£Ê½, ²¨ÌØÂÊ500Kbps */
//            if (mode == 0)  /* ÆÕÍ¨Ä£Ê½, ÐèÒª2¸ö¿ª·¢°å */
//            {
//							printf("\r\n start motor \r\n");
//							start_res = can_send_msg(motorId, start_motor, 8);
//							start_res = can_send_msg(motorId, start_motor, 8);
//							show_res(start_res);							
//            }
//            else            /* »Ø»·Ä£Ê½,Ò»¸ö¿ª·¢°å¾Í¿ÉÒÔ²âÊÔÁË. */
//            {
//							printf("\r\n close motor \r\n");
//							stop_res = can_send_msg(motorId, stop_motor, 8);
//							show_res(stop_res);
//            }
//        }
//				else if (key == KEY1_PRES)
//				{
//					printf("\r\n stop motor \r\n");
//					stop_res = can_send_msg(motorId, stop_motor, 8);
//					stop_res = can_send_msg(motorId, stop_motor, 8);
//					show_res(torque_res);
//				}
//				else if (key == KEY2_PRES)
//				{
//					printf("\r\n close motor \r\n");
//					torque_res = can_send_msg(motorId, close_motor, 8);
//					torque_res = can_send_msg(motorId, close_motor, 8);
//					show_res(torque_res);
//				}

//        rxlen = can_receive_msg(0x12, canbuf);  /* CAN ID = 0x12, ½ÓÊÕÊý¾Ý²éÑ¯ */

//        if (rxlen) /* ½ÓÊÕµ½ÓÐÊý¾Ý */
//        {
////            lcd_fill(30, 270, 130, 310, WHITE); /* Çå³ýÖ®Ç°µÄÏÔÊ¾ */

//            for (i = 0; i < rxlen; i++)
//            {
//                if (i < 4)
//                {
////                    lcd_show_xnum(30 + i * 32, 250, canbuf[i], 3, 16, 0X80, BLUE);          /* ÏÔÊ¾Êý¾Ý */
//									usart_show_xnum(canbuf[i], 3);
//                }
//                else
//                {
////                    lcd_show_xnum(30 + (i - 4) * 32, 270, canbuf[i], 3, 16, 0X80, BLUE);    /* ÏÔÊ¾Êý¾Ý */
//										usart_show_xnum(canbuf[i], 3);
//                }
//            }
//        }
//				torque_res = can_send_msg(motorId, torque_control_2, 8);
//        t++;
//        delay_ms(10);

//        if (t == 20)
//        {
//            LED0_TOGGLE();  /* ÌáÊ¾ÏµÍ³ÕýÔÚÔËÐÐ */
//            t = 0;
//            cnt++;
////            lcd_show_xnum(30 + 48, 150, cnt, 3, 16, 0X80, BLUE);                            /* ÏÔÊ¾Êý¾Ý */
////						usart_show_xnum(cnt, 3);
//        }
```

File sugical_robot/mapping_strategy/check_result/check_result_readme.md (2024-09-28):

# check_result_readme

TODO：

应该写一个main函数，作为check过程的路口

## 代码说明

* 
* five_joint_arm_simu_code：用于在matlab中绘制主端结构
* get_T_con_from_mapping：字面意思，根据[theta3,theta_4,thtea_5]得到从端对应旋转矩阵
* master_DH_model： 所有以这个开头的均为在matlab中绘制图像
* slave_DH_model: 为了推导末端在x,z方向上的分量，可以试着先把末端的其次变换矩阵求出来
* modified_DH  +  standard_DH 这是为了求解单个齐次变换
* 

为了验证论文映射的正确性，需要干一下几件事

* 总结主从两端的简易DH表
* 根据这个DH在matlab中绘制机器人模型

## 构建主从端 DH表



| i    | link | $a_{i-1}$ | $\alpha_{i-1}$ | $d_i$                                 | $\theta_i$                                      |
| ---- | ---- | --------- | -------------- | ------------------------------------- | ----------------------------------------------- |
| 1    | 0=>1 | 0         | $\pi/2$        | 0                                     | <font color = red>$\theta_1^*  $</font>         |
| 2    | 1=>2 | 0         | $-\pi/2$       | <font color = red>**$d_2^*$**</font > | 0                                               |
| 3    | 2=>3 | 0         | $\pi/2$        | h                                     | <font color = red>$\theta_3^* + \pi/2 $</font>  |
| 4    | 3=>4 | 0         | $\pi/2$        | 0                                     | <font color = red>$\theta_4^*  + \pi/2 $</font> |
| 5    | 4=>5 | 0         | $\pi/2$        | $l$                                   | <font color = red>$\theta_5^* + \pi/2 $</font>  |

单独分析连杆部分

以下是**modified**版本 DH建模（根据建模方法编写了一个modified_DH函数，用于计算给定四个参数时的其次变换矩阵）

| i    | $a_{i-1}$ | $\alpha_{i-1}$ | $d_i $ | $\theta_i$           |
| ---- | --------- | -------------- | ------ | -------------------- |
| 3    | 0         | $\pi/2$        | h      | $\theta_3^* + \pi/2$ |
| 4    | 0         | $-\pi/2$       | 0      | $\theta_4^* - \pi/2$ |
| 5    | 0         | $-\pi/2$       | l      | $\theta_5^* $        |

成功计算了末端的位姿

## 构建从端DH表



虽然论文用的std方法，但是md方法肯定也是一样的

注：为了方便表达，之后 ks 统统记为 \alpha

7-29发现从端与主端坐标系规定不同， 略作修改；

| link(i) | $a_{i-1}$ | $\alpha_{i-1}$ | $d_i$ | $\theta_i$   |
| ------- | --------- | -------------- | ----- | ------------ |
| 0=>1    | 0         | 0              | $D_1$ | 0            |
| 1=>2    | 0         | $\pi/2$        | 0     | $\alpha_2/2$ |
| 2=>3    | 0         | $-\pi/2$       | $d_2$ | 0            |
| 3=>4    | 0         | $\pi/2$        | 0     | $\alpha_2/2$ |
| 4=>5    | 0         | $-\pi/2$       | 0     | $\Phi_3$     |
| 5=>6    | 0         | $\pi/2$        | 0     | $\alpha_4/2$ |
| 6=>7    | 0         | $-\pi/2$       | $d_4$ | 0            |
| 7=>8    | 0         | $\pi/2$        | 0     | $\alpha_4/2$ |
| 8=>9    | 0         | $-\pi/2$       | 0     | $-\Phi_3$    |
| 9=>10   | 0         | 0              | $l$   | $\Theta_5$   |

$d_2 =  \frac{2s_1}{\alpha_2} sin(\alpha_2/2)$ ; $d_4 =  \frac{2s_2}{\alpha_4} sin(\alpha_4/2)$

## md 法对连续体建模

先生成std法的table，然后用gpt生成的std函数验证一下没问题

下面是尝试使用md法构建的table

| link | $a_{i-1}$ | $\alpha_{i-1}$ |  $d_i$  |  $\theta_i$   |
| :--: | :-------: | :------------: | :-----: | :-----------: |
|  1   |     0     |       0        |    0    | $\theta_1 ^*$ |
|  2   |     0     |     -pi/2      |    0    | $\theta_2^*$  |
|  3   |     0     |      pi/2      | $d_3^*$ |       0       |
|  4   |     0     |     -pi/2      |    0    | $\theta_4^*$  |
|  5   |     0     |      pi/2      |    0    | $\theta_5^*$  |

# DH method





相同点是，至少关节和连杆之间的关系是一样的：

* n个关节的机器人，有n+1 个连杆，关节 i 连接 连杆i-1 和 连杆 i，也就是关节 i 在连杆 i-1 的末端，负责驱动连杆i 
* 两种方法dh参数的第i行，实际上都是描述坐标系 {O_i-1} 到 坐标系{O_i} 之间的变化

## Standard_DH

* 首先也是坐标系z_i 的配置，标准法规定z_i是关节i+1的驱动轴，关节i被驱动，坐标系Oi会跟着运动
* 然后x轴需要与前一个坐标系z轴垂直且相交，上面说是与前一个z叉乘（我看是不是）分三种情况讨论

四个参数：

*  **a** 是轴 $z_i$ 与 $z_{i+1}$之间沿轴线 $x_{i+1}$ 之间的距离
*  **$\alpha$** 是垂直于 $x_{i+1}$ 平面测得两个z轴之间的夹角，正向从 i 到 i+1
*  **d** 是从坐标系i原点o到轴线 $x_{i+1}$与$z_i$交点 o' 之间的距离
*  **$\theta$** 是垂直于$z_i$平面从两个x轴之间的夹角，同样遵循从低到高为＋

## Modified_DH

之前总结过std_DH的建模方法，这一次看看md_DH:

* 首先是坐标系z的配置，同样是z_i 对应关节轴i，不过关节轴i对应连杆i的起始端
* x_i的配置略有不同，x_i 由关节轴 i 、i+1 共同决定，由关节轴 i 指向 i+1（a_i，两个关节轴的公垂线） ，当a_i = 0时，也即两个坐标系重合时， x_i = z_i+1 x z_i
* y就是右手定则确定了

四个参数：

* $a_i$ : zi 到 zi+1 沿 xi 的距离
* $\alpha_i$ : zi => zi+1 的角度，以 xi 为轴
* $d_i$ :xi-1 到到xi 沿 zi的距离
* $\theta_i$  :   xi-1 到 xi 绕 zi 旋转的角度

前面两个是从zi到 z_i+1，参考轴都是 x i :

后面两个参数 是x  i-1 到 xi, 参考轴是 zi 

所以表格四个参数是 $a_{i-1}$$\alpha_{i-1}$$d_i $$\theta_i$ => 最后四个参数其实还是描述 $\{O_{i-1}\}$ 到 $\{O_{i}\}$

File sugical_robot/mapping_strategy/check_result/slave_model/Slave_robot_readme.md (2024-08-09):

# Slave_robot_readme

这个文件夹主要用来求解从端手术臂相关的运动学模型

* derive_slave_T : 求解基于CPP方法建立的DH模型对应的其次变换矩阵
* 使用3D绘图的方法验证DH表的正确性
*

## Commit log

2024-02-19 Create 科研手册1-26.md
    test
2024-02-19 2-19添加一些readme
2024-02-19 更新readme
2024-02-20 2-20-写论文introduce
2024-02-22 2-22更新
2024-02-23 2-23改完introduce，写完机械设计，写了一部分消抖
2024-03-13 3-13：完成电机和编码器调试
2024-03-14 去东京前干完了tremor部分的实验和结果
2024-03-25 只差一张实物图片了
2024-03-30 3-30更新
2024-04-01 4-1更新
2024-04-29 劳资五一要出去玩
2024-05-23 5-23双臂系统
2024-06-25 6-25
    好像又多了很多东西
    [base_link.STL, cylinderJointD1.STL, cylinderJointD1_c.STL, cylinderJointD1_c1.STL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]
2024-08-09 完成运动学映射
    开题答辩结束，进入第二阶段吧
2024-08-18 去马来西亚度假咯
2024-11-15 add some research results for tremor depression
    [1017-track-nosp-tired.csv, 1017-track-nosp.csv, 1017-track-sp-tired.csv, 1017-track-sp.csv]
2025-02-27 准备整理一下电控
    2-27日整理仓库前更新
2025-02-27 尝试看看ignore
2025-02-27 ignore 没用
